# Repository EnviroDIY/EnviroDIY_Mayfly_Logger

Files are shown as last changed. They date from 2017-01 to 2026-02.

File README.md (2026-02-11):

EnviroDIY Mayfly Data Logger
==============
The [EnviroDIY™ Mayfly Data Logger](http://envirodiy.org/mayfly/) is an Arduino-framework microcontroller board designed specifically for environmental Internet of Things (IoT) applications with the goal to facilitate professional-quality, do-it-yourself (DIY) environmental science and monitoring.

This [EnviroDIY_Mayfly_Logger Github repository](https://github.com/EnviroDIY/EnviroDIY_Mayfly_Logger) provides hardware design files and example code sketches, the [EnviroDIY community](https://www.envirodiy.org) provides support via project posts and forums, and the [Mayfly Logger board is available for purchase on the [EnviroDIY Shop](https://www.envirodiy.org/shop/) for user convenience.

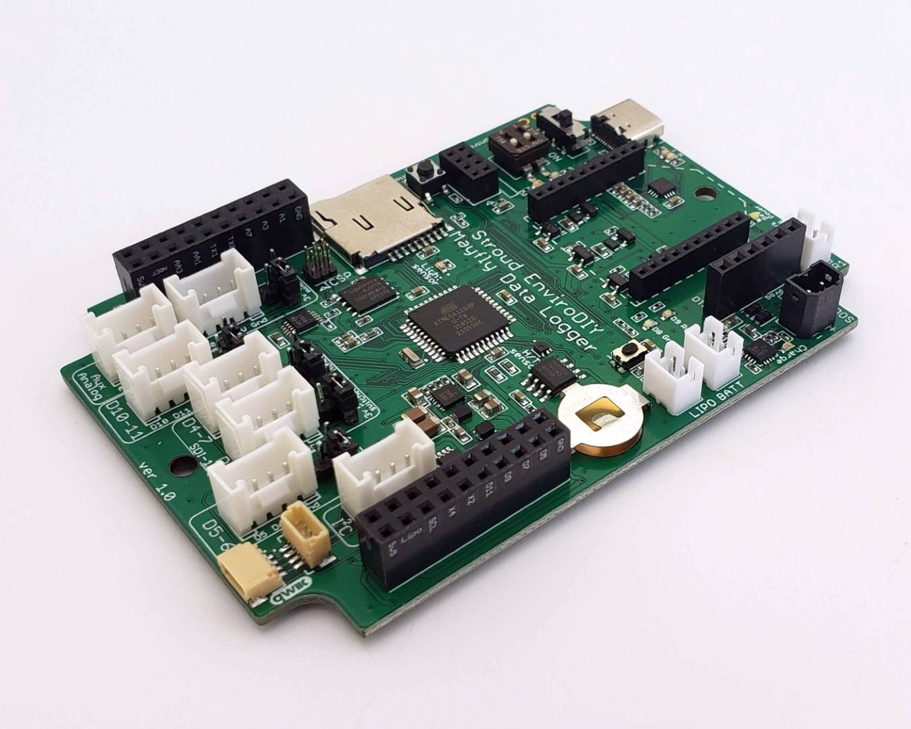
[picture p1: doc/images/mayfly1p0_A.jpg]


## Features:

- ATmega1284p processor
    - 128kB program (flash) memory, 16kB RAM
    - 2 UART, 1 I2C, 1 SPI connection
    - 32 total I/O pins
    - 3.3V, 8MHz operating frequency
- Integrated 6V solar lipo battery charger
- Precise real time clock (RTC, [DS3231](https://datasheets.maximintegrated.com/en/ds/DS3231.pdf)) with separate power supply
- Auxillary 16 bit ADC ([TI ADS1115](http://www.ti.com/lit/ds/symlink/ads1114.pdf))
- FTDI chip for USB communication via USB-C port
- microSD memory card socket
- XBee radio/wifi/cellular module socket
- 7 [Grove](http://wiki.seeedstudio.com/Grove_System/) connectors with access to I2C, auxillary ADC, and digital pins
- 0.5A switchable power supply for sensors at 3.3V and 5V, and 0.15A at 12V
- On-board power switch
- Two controllable LED's (red and green)
- One programmable push-button
- Onboard humidity/temperature sensor and analog light sensor
- Onboard auxiliary 8MB flash memory chip

## Pin-out for v1.x

| Pin Number[s] | Function             | Access                                 | Notes |
|---------------|----------------------|----------------------------------------|-------|
| D0/D1         | Serial Rx/Tx (UART)  | Connected to FTDI for USB programming  | Also accessible via programming port, 20 pin header, and XBee socket via SJ8/9 |
| D2/D3         | Serial1 Rx/Tx (UART) | XBee socket Din/Dout (pins 2/3)        | Also accessible via 20 pin header, can be disconnected from XBee socket via SJ8/9 |
| D19           | XBee CTS             | XBee socket CTS (pin 12)               | Also accessible via 20 pin header |
| D20           | XBee RTS             | XBee socket RTS (pin 16)               | Also accessible via 20 pin header |
| D23           | XBee DTR             | XBee socket DTR (pin 9)                | Also accessible via 20 pin header |
| A5=D29*       | XBee Assoc or RI     | XBee socket Assoc or RI (pin 15 or 20) | Not connected to XBee socket by default, use SJ7 to connect; Also accessible via 20 pin header |
| D16/D17       | I2C SCL/SDA ("Wire") | Grove connector                        | Also accessible via 20 pin header |
| D13/D14/D15   | SPI MOSI/MISO/SCK    | microSD card slot & SPI header         |  |
| D12           | microSD chip select  | microSD card slot & SPI header         |  |
| D18           | SD card detect OR RTC 32KHz | 20 pin header                   | Not connected to either SD or RTC by default, use SJ6 for RTC or SJ10 for SD, _do not use both_ |
| A7=D31 _or_ D10 | RTC Interrupt      | 20 pin header                          | A7 is connected to RTC interrupt by default; Use SJ1 to disconnect A7 and/or to connect D10 |
| D22           | Switched power/LED4  | Switched power on all Grove ports      | Pin is not directly accessible, only switched power; Cut SJ3 to disconnect LED4 (red) |
| D21           | user push button     | 20 pin header                          | Cut SJ to disconnect button |
| D8            | LED1 (green)         | 20 pin header                          |  |
| D9            | LED2 (red)           | 20 pin header                          |  |
| A6=D30        | Battery measurement  | None                                   | Connected via voltage divider |
| D4-7, D10-11  | General Purpose I/O  | Grove connector; 20 pin header         |  |
| AA0-AA3       | Auxilliary ADC       | Grove connector; 20 pin header         | Connected to _Auxillary_ adc (TI ADS1115), not to Mayfly analog pins |

## Solder Jumper Connections for v1.x

| Number | Function                        | Default Connection                |
|--------|---------------------------------|-----------------------------------|
| SJ1    | Connect to interrupt from RTC   | Pin A7 connected to RTC interrupt       |
| SJ2    | Disconnect D21 from user button | Pin D21 is connected to button (closed) |
| SJ3    | Disconnect D22 from LED3        | Pin D22 is connected to LED3 (closed)   |
| SJ4    | Disconnect LED4 from solar      | LED4 indicates solar charging status (closed) |
| SJ7    | Pin A5 to XBee ASSOC _or_ RI    | Not connected (all pads open)                 |
| SJ8    | XBee Din to TX0/TX1             | XBee Din connected to TX1                     |
| SJ9    | XBee Dout to RX0/RX1            | XBee Dout connected to RX1                    |
| SJ12   | D10 external pull-up            | D10 (INT2) is not pulled up externally (open) |

## Programming

Mayfly Data Logger can be programmed using standard Aruduino code and community libraries via the [Arduino Integrated Development Environment (IDE) software](https://www.arduino.cc/en/Main/Software) or the more powerful [PlatformIO](https://platformio.org) extensions for [Visual Studio Code](https://code.visualstudio.com/) or [Atom](https://atom.io/).

To use the Mayfly with the Arduino IDE you must add "EnviroDIY ATmega Boards" using the Tools > Board > Boards Manager as described in the [Mayfly Data Logger Software](http://envirodiy.org/mayfly/software/) post

No addition set-up is required to use the PlatformIO.
The proper enviroment settings for the Mayfly in a platformio.ini file are:

```ini
[env:mayfly]
platform = atmelavr
board = mayfly
framework = arduino
```

## Additional Resources and Links

- Read the [Getting Started With the Mayfly Data Logger](http://envirodiy.org/mayfly/) page on the EnviroDIY community website for guidance for beginners with the Mayfly, sensor station maintence, and data management.
- Make use of the [The EnviroDIY Mayfly Data l=Logger Forum](https://www.envirodiy.org/forum/mayfly-data-logger/) to ask and answer questions about the Mayfly
- Learn Mayfly basics following our [Mayfly Data Logger Software](http://envirodiy.org/mayfly/software/) post and running the example and workshop code sketches, using the Arduino IDE (from File > Sketchbook), from our [EnviroDIY_Mayfly_Logger > examples](https://github.com/EnviroDIY/EnviroDIY_Mayfly_Logger/tree/master/examples) or [EnviroDIY_Mayfly_Logger > workshop](https://github.com/EnviroDIY/EnviroDIY_Mayfly_Logger/tree/master/workshop) folders.
- Advance your capabilities to deploy solar-powered environmental monitoring stations with our [LearnEnviroDIY tutorial](https://envirodiy.github.io/LearnEnviroDIY/)
- Utilize the [ModularSensors](https://github.com/EnviroDIY/ModularSensors) code library and other [EnviroDIY libraries on GitHub](https://github.com/EnviroDIY) for datalogging built around the Mayfly
- Find and attend a training workshop for do-it-yourself environmental monitoring built around the Mayfly by contacting the Stroud Water Research Center's [citizen science outreach](https://stroudcenter.org/people/bressler/) or [education](https://stroudcenter.org/education/contact/) departments.

## Design Files & Further Documentation

We share our EnviroDIY Mayfly logger hardware design files and documentation in this repository's [Hardware Design Files](hardware) pages and [Documentation](doc) pages.

## License
Software sketches and code are released under the BSD 3-Clause License -- See [LICENSE.md](https://github.com/EnviroDIY/EnviroDIY_Mayfly_Logger/blob/master/LICENSE.md) file for details.

Documentation is licensed as [Creative Commons Attribution-ShareAlike 4.0](https://creativecommons.org/licenses/by-sa/4.0/) (CC-BY-SA) copyright.

Hardware designs shared are released, unless otherwise indicated, under the [CERN Open Hardware License 1.2](https://www.ohwr.org/projects/cernohl/wiki) (CERN_OHL).

## Credits
[EnviroDIY](http://envirodiy.org/)™ is presented by the Stroud Water Research Center, with contributions from a community of enthusiasts sharing do-it-yourself ideas for environmental science and monitoring.

[Shannon Hicks](https://github.com/s-hicks2) is the primary developer of the EnviroDIY Mayfly Data Logger hardware, with input from many [other contributors](https://github.com/EnviroDIY/EnviroDIY_Mayfly_Logger/graphs/contributors).

The Mayfly was developed based on the [SODAQ Mbili board](https://support.sodaq.com/sodaq-one/sodaq-mbili-1284p/) hardware and the [SODAQ Mbili bootloader](https://github.com/SodaqMoja/HardwareMbili) software, designed by Gregory Knauff (GKNFF).

This project has benefited from the support from the following funders:

* William Penn Foundation
* US Environmental Protection Agency (EPA)
* National Science Foundation, awards [EAR-0724971](http://www.nsf.gov/awardsearch/showAward?AWD_ID=0724971), [EAR-1331856](http://www.nsf.gov/awardsearch/showAward?AWD_ID=1331856), [ACI-1339834](http://www.nsf.gov/awardsearch/showAward?AWD_ID=1339834)
* Stroud Water Research Center endowment

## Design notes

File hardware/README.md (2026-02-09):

Hardware Design Files
==============

Here we provide EnviroDIY Mayfly design files including:
- EAGLE PCB electronic design files for use with the EAGLE electronic design automation (EDA) software (a [free maker edition](https://www.autodesk.com/products/eagle/compare) is available).
- Board schematic images, for versions 0.3, 0.4, 0.5, 0.5b, 1.0, 1.1revA, and 1.1revB.

See our [Documentation](https://github.com/EnviroDIY/EnviroDIY_Mayfly_Logger/tree/master/doc) pages for a [Feature List](https://github.com/EnviroDIY/EnviroDIY_Mayfly_Logger/blob/master/doc/Intro_GettingStarted.md), for details on [Board Features](https://github.com/EnviroDIY/EnviroDIY_Mayfly_Logger/blob/master/doc/Hardware_BoardFeatures.md), and for [Jumper Settings](https://github.com/EnviroDIY/EnviroDIY_Mayfly_Logger/blob/master/doc/Hardware_JumperSettings.md).

For questions, use our Q&A forum at https://envirodiy.org/forum/mayfly/.

## Hardware Design Credits

The Mayfly Logger was developed by [Shannon Hicks](https://github.com/s-hicks2) and based on the [SODAQ Mbili board](https://support.sodaq.com/sodaq-one/sodaq-mbili-1284p/) hardware and the [SODAQ Mbili bootloader](https://github.com/SodaqMoja/HardwareMbili) software designed by Gregory Knauff (GKNFF).

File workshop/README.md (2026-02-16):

Example sketches used in workshops with the EnviroDIY Mayfy Data Logger v1.x boards.

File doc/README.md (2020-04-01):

Documentation
==============
The documentation contained in this folder are based on documentation provided by the EnviroDIY community website at https://www.envirodiy.org/mayfly/. These are:

- #### [Hardware: Feature List](https://github.com/EnviroDIY/EnviroDIY_Mayfly_Logger/blob/master/doc/Intro_GettingStarted.md)
  - #### [Board Features](https://github.com/EnviroDIY/EnviroDIY_Mayfly_Logger/blob/master/doc/Hardware_BoardFeatures.md)
  - #### [Jumper Settings](https://github.com/EnviroDIY/EnviroDIY_Mayfly_Logger/blob/master/doc/Hardware_JumperSettings.md)

- #### [Software](https://github.com/EnviroDIY/EnviroDIY_Mayfly_Logger/blob/master/doc/Software_Intro.md)

See this repository's [Hardware Design Files](hardware) pages for [Board schematics](https://github.com/EnviroDIY/EnviroDIY_Mayfly_Logger/blob/master/hardware) and [EAGLE PCB electronic design files](https://github.com/EnviroDIY/EnviroDIY_Mayfly_Logger/blob/master/hardware/Mayfly_v0p5b).

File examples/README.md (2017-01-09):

Example Arduino Sketches for the Mayfly Board
==============

All of the Mayfly boards have been pre-programmed with an initial demonstration sketch, named "initial\_demo\_blink_temperature".  When you first connect power to the board, and turn the board on (switch on upper left) you will see the red and green LEDs blinking.

You can also see the real-time temperature of your Mayfly board if you [connect the Mayfly to your computer and configure the Arduino IDE to communicate with it](https://github.com/EnviroDIY/Arduino_boards). Once the Arduino IDE is configured to communicate with your Mayflay board, open the [Serial Monitor button (button on upper right of any sketch)](https://lh6.googleusercontent.com/GO9HQ1q3v4ho-H7ZqP55cQ4o_nLdyYpkCauIWOvN5xrQAMNIfgeiu_LiRTfAN2yruvjBLGMNrACzWffwhlM5ADSem35dDPpI9Mj5WWN-l8YSizSh-3HwvPEwtzAo3o0ZZjJgAyw), and change the serial communication rate at 57600 baud. You will see the current board temperature as measured by the DS3231 Real Time Clock chip's internal temperature sensor, updated every second.

Try out some of the other examples sketches shared here!

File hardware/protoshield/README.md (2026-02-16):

EagleCAD files for the Mayfly Protoshield v1 (discontinued in 2020)

NOTE:  This ProtoShield is only compatible with the older Mayfly v0.5b boards.  It is not compatible with the newer Mayfly v1.0 or v1.1 board due to changes in the pinouts of the headers.  Do not attempt to use this ProtoShield with a Mayfly v1.0 or v1.1 board or damage to the Mayfly and/or ProtoShield will occur.

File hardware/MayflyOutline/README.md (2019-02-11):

EagleCAD file for basic ouline of the Mayfly board with headers (v0.3, v0.4, v0.5, v0.5b)

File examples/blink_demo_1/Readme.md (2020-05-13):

# Blinking LED's: Version 1

This example program:
- Turns on an LED on for one second, then off for one second, repeatedly.
- Introduces use of variables.
- Includes Serial Monitor readout in setup function.

This is blink demo is designed for first-time users of Arduino and the EnviroDIY Mayfly logger.

The Mayfly has two LED lights attached to digital pins 8 and 9.
Both lights can be controlled using code with the ```pinMode``` and ```digitalWrite``` functions.

## Stepping through the code

Arduino sketches (really c++ programs) begin with a list of the outside libraries needed to run the sketch.
These libraries must be installed on your .../Arduino/libraries directory for the sketch to run.
This example only uses one library, the Arudino framework library (```Arduino.h```).
We include that library with the following code:
```cpp
#include <Arduino.h>
```

After including the Arduino framework, we name some "global variables" for the sketch.
This variables list is located before the functions and defines the variables for the sketch.
Variables are useful for assigning information once at the beginning of a sketch, because most sketches will need to repeat information like pin locations.
Notice that the sketch re-uses the value ```delayTime``` four times.
The text ```int``` before the name of the variable specifies integer data type.

Try modifying the delay time and LED pin and re-running the sketch.
```cpp
int delayTime = 1000;   // milliseconds, so 1000 = one second
```

Assign pin numbers for built-in LEDs.
```cpp
int LED_BUILTIN_green = 8;  // Mayfly has a green LED connected to digital pin 8
int LED_BUILTIN_red = 9;    // Mayfly has a red LED connected to digital pin 9
```

The "setup" function runs once when you press reset or power the board.
The "returned value" for this function is "void", which means it doesn't return a value, the function simply performs an action.
```cpp
void setup ()
{
    pinMode(LED_BUILTIN_green, OUTPUT);  // set the pin as output to turn on the LED
    pinMode(LED_BUILTIN_red, OUTPUT);    // all you need to set up the LED blink
    delay(delayTime);
    Serial.println("Mayfly: Blink demo 1");  // sends a message to the Serial Monitor
    delay(delayTime);
}
```

The "loop" function runs over and over again.
It performs an action wouthout returning a value, so "void" is once again used in the function declaration.
```cpp
void loop ()
{
    digitalWrite(LED_BUILTIN_green, HIGH); // turn the green LED on (HIGH is the voltage level)
    digitalWrite(LED_BUILTIN_red, LOW);    // and turn the red LED off (LOW is the voltage level)
    delay(delayTime);                      // wait for the time specified in delayTime variable
    digitalWrite(LED_BUILTIN_green, LOW);  // now turn the green LED off by making the voltage LOW
    digitalWrite(LED_BUILTIN_red, HIGH);   // and turn the red LED on
    delay(delayTime);                      // wait for the time specified in delayTime variable
}
```

## Notes

This demo assumes you have installed the proper drivers to connect to the Mayfly.
If you need a resource for getting started with Arduino, the tutorial by Adafruit at https://learn.adafruit.com/series/ladyadas-learn-arduino will get you connected and running a blink demo in about an hour.

To run this demo you will need to first connect to the Mayfly by specifying your board under
Tools>Board (select appropriate Mayfly board) and specifying which communication port to use
under Tools>Port.

Once connected to the Mayfly, you need to Verify/Compile the sketch by clicking the checkmark at the top, left corner of the Arudino app window. If there is an error, it will appear (in orange) below.
If there are no errors, the window color will not change and it will read "Done compiling."
Always compile before uploading a sketch to your Arduino.
Once compiled, click on the right arrow button to upload the sketch to the Mayfly.
If it worked, the LED lights on the board will begin to blink.

## Credits

Original sketch:
- modified 8 May 2014 by Scott Fitzgerald
- modified 2 Sep 2016 by Arturo Guadalupi
- modified 8 Sep 2016 by Colby Newman for Mayfly:
- modified 7 Jun 2017 by Beth Fisher github.com/fisherba

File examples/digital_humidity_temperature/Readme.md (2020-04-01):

# Reading digital temperature and humidity

This example program:
- Communicates with a digital temperature/humidity board (DHT11)
- Writes the output to the serial port at one second intervals

Written for Mayfly logger and Grove digital temperature/humidity board based on the AOSong DHT (DHT11), with options for DHT 21 and 22.

## Physical connections

- Connect pin 1 (on the left) of the sensor to +5V
- Connect pin 2 of the sensor to whatever your DHTPIN is
- Connect pin 4 (on the right) of the sensor to GROUND
- Connect a 10K resistor from pin 2 (data) to pin 1 (power) of the sensor

## Stepping through the code

Arduino sketches (really c++ programs) begin with a list of the outside libraries needed to run the sketch.
These libraries must be installed on your .../Arduino/libraries directory for the sketch to run.
This example only uses two libraries, the Arudino framework library (```Arduino.h```) and the Adafruit library for the AOSong DHT (```DHT.h```).
We use the include that library with the following code:
```cpp
#include <Arduino.h>
#include <DHT.h>
```

After including the libraries, we define exactly which type of sensor we're using and the pin it is connected to.
We then create an "object" in the processor's memory representing the functionality of the DHT sensor.
```cpp
#define DHTPIN 10       // Specifies the pin connected to the DHT signal.
#define DHTTYPE DHT11   // DHT 11

DHT dht(DHTPIN, DHTTYPE);
```

The "setup" function runs once when you press reset or power the board.
The "returned value" for this function is "void", which means it doesn't return a value, the function simply performs an action.
In this setup function, we are providing power to the DHT sensor by turning on pin 22.
We are also writing a note to the serial port to appear on the serial monitor.
The last function performs necessary setup for the DHT.
Because we are using a library of functions to communicate with the DHT, we do not need to specify exactly what commands are needed to prepare the DHT.
We call the begin function for the dht object in memory and take advantage of the set-up code provided by that library.
```cpp
void setup()
{
    pinMode(22, OUTPUT);      // pin D22 is the enable line for the Mayfly's switched 3.3/5v power lines
    digitalWrite(22, HIGH);   // set this pin high and leave it on for the rest of the sketch
    delay(200);
    Serial.begin(57600);
    Serial.println("Digital Humidity/Temperature");

    dht.begin();
}
```

The "loop" function runs over and over again.
It performs an action wouthout returning a value, so "void" is once again used in the function declaration.
As in the set-up, we rely on the DHT library to figure out the details of talking to the DHT and call that libraries functions to get the results of the reading.
We print the readings to the serial monitor.
```cpp
void loop()
{
    // Reading temperature or humidity takes about 250 milliseconds
    // Sensor readings may also be up to 2 seconds old
    float h = dht.readHumidity();
    float t = dht.readTemperature();

    // check if returns are valid, if they are NaN (not a number) then something went wrong
    if (isnan(t) || isnan(h))
    {
        Serial.println("Failed to read from DHT");
    }
    else
    {
        Serial.print("Humidity: ");
        Serial.print(h);
        Serial.print(" %\t");
        Serial.print("Temperature: ");
        Serial.print(t);
        Serial.println(" *C");
    }
}
```

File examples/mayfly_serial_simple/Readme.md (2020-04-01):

# A simple serial example

This example program:
- Sends data to the computer via the FTDI chip on Serial
- Sends data to an XBee via Serial 1

## Stepping through the code

Arduino sketches (really c++ programs) begin with a list of the outside libraries needed to run the sketch.
These libraries must be installed on your .../Arduino/libraries directory for the sketch to run.
This example only uses one library, the Arudino framework library (```Arduino.h```).
We use the include that library with the following code:
```cpp
#include <Arduino.h>
```

The "setup" function runs once when you press reset or power the board.
The "returned value" for this function is "void", which means it doesn't return a value, the function simply performs an action.
In this setup function, we are deciding at what speed the board will communicate and printing out text.
```cpp

void setup()
{
  Serial.begin(57600);  // Start the serial connection with the computer (UART-0)

  Serial1.begin(9600);  // Start the connection on the Mayfly's Xbee port (UART-1)
}

```

The "loop" function runs over and over again.
It performs an action wouthout returning a value, so "void" is once again used in the function declaration.
This functio merely prints some text to the serial monitor and to the XBee socket with a short delay in between.
```cpp
void loop()
{

 Serial.println("This is Serial Data printed to the computer");

 delay(500);

 Serial1.print("This is Serial Data sent to the Xbee port");

 delay(5000);
}
```

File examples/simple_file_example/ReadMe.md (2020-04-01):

# Simple File Example

This example program demonstrates reading the battery voltage on the LiPo attached to the Mayfly and writing that value to a file on a SD card.

NOTE:  This program is for demonstration only.  It is NOT intended to be used for environmental monitoring.  It does not contain any of the necessary code to allow the Mayfly to sleep and reduce power between readings.

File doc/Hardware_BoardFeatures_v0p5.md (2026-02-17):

Board Features for v0.5b
==============
The Mayfly Data Logger board has many unique features and hardware options. Learn more below!

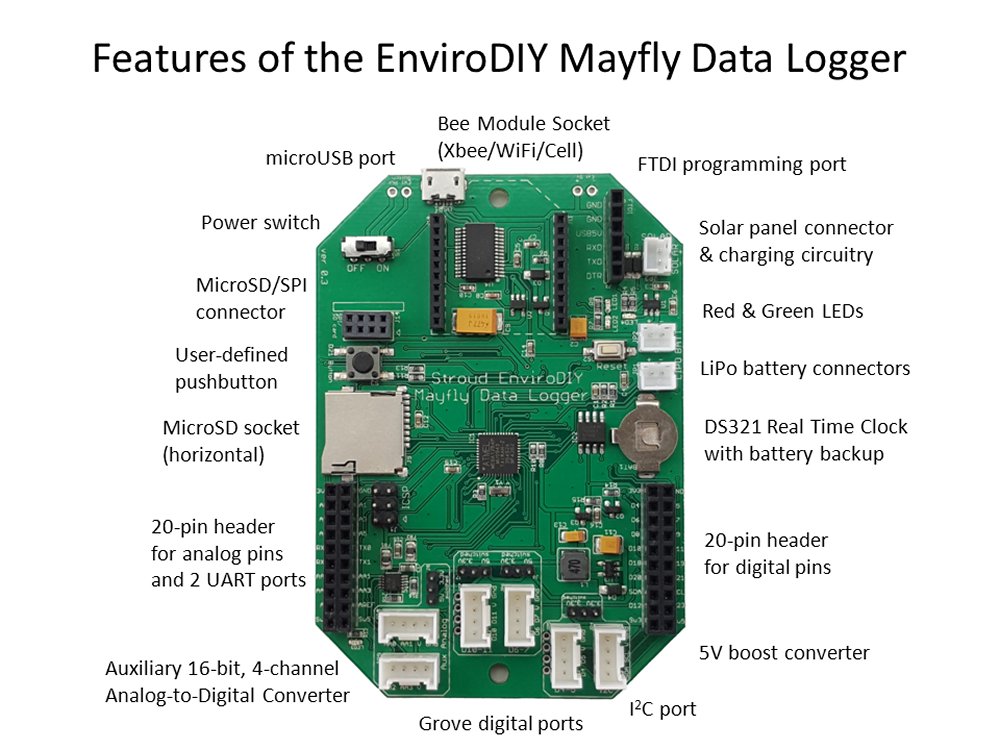
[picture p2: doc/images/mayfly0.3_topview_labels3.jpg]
Mayfly v0.3 Top View with Labels


## Features of the EnviroDIY Mayfly Data Logger version 0.5b

The microUSB port is used to program the Mayfly via your computer.
Once the board has been programmed, you can also supply power to the Mayfly with any microUSB cable or mobile phone charger that provides 5vDC.

The Bee socket is compatible with any module that use the standard Bee connection footprint.
Modules include Xbee radio modules, GPRSBee cell phone board, and other modules for WiFi or Bluetooth communication.

A 6-pin header is available for programming the board via a standard FTDI interface board or programming cable.
Be sure to observe the polarity and connect the FTDI adapter in the right orientation.

Any 6-volt solar panel can be connected to the JST socket for charging a standard 3.7v LiPo battery.
A yellow LED will light up whenever there is sufficient sunlight to charge the battery.

Two LEDS (one green, one red) are connected to pins D8 (green) and D9 (red) for full user control.

Two JST connectors are labeled LiPo (lithium polymer) battery power connections.
Connect a standard 3.7v LiPo battery to either port.
You should only connect one battery to the Mayfly.
The second port is for devices like the GPRSbee that need a direct connection to the battery.
More information about using the GPRSbee will be provided soon.

The DS3231 Real Time Clock chip needs a small battery to keep it’s clock running when the Mayfly isn’t powered by a main battery.
Insert a CR1220 3v lithium battery (with the + side facing up).
Users who don’t want to keep the RTC backed up can omit the battery.

Two 20-pin headers with standard 0.1″ pin spacing provide access to all of the available pins.

A voltage boost circuit provides a 5 volt supply that can be switched on or off by using pin D22.
This pin is also used to turn the “3.3v_Switched” output on or off.

Grove connectors provide easy interface to 4 groups of digital pins. Three of the connectors contain digital pins (4, 5, 6, 7, 10, and 11) and the forth connector is for I2C protocol.
Note:  on board versions 0.3 and 0.4, the I2C connector has the proper pin order found on all Grove I2C ports, but the white silkscreen printing on the board has the SDA and SCL pins reversed.
The pins are correct, only the printing is swapped.
The printing is correct on version 0.5.

Two more Grove connectors interface with the ADS1115 auxiliary 16-bit A/D converter.

The data card socket on the Mayfly accepts standard microSD memory cards.

The pushbutton is connected to digital pin D21.
Users can have their sketch look for a state change on that pin to provide input to the system.

A small 2×4 header allows users to connect the custom Mayfly microSD right-angle adapter board.
This handy accessory allows you to easily access the memory card when the Mayfly is mounted in an enclosure where the usual horizontal slot is inaccessible.
Do not use a memory card in both sockets at the same time.
Users could also build their own custom adapter boards for this header since it breaks out all of the necessary SPI pins.

## New features on version 0.5:
In March 2017, we released version 0.5.
Here are the main difference between 0.5 and the earlier versions:

- Separate 3.3v regulator on the Switched3.3v bus (makes the board more stable when switching loads on and off, and increase current output available to the load with a max output of 500ma)
- New 5v-boost regulator (SC4503 replaces the obsolete NCP1402)
- Onboard pullup resistor (1M ohm) available via jumper SJ12 for connecting D10 to the pullup (useful for using D10 as a hardware interrupt)
- External voltage input range improved – now accepts 4 to 12v.
A small slide switch on the top of the board allows you to select the usual USB/Lipo power option, or you can select an external voltage source to power the board.
To prevent over-voltage damage, the USB port is disconnected from the Mayfly when the switch is set to “Ext”.
If you are using the Mayfly with an external battery and then want to reprogram the Mayfly, you’ll need to slide the switch to “USB/Lipo” in order to program the board.
Then slide it back to “Ext” to power the board via your external source.
If you have a Lipo battery connected to the “Lipo Batt” JST headers, be sure to keep the slide switch in the “USB/Lipo” position or the board will not be powered.

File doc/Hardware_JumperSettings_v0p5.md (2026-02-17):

Jumper settings for v0.5b
==============
On the back of the Mayfly v0.5b board, there are 12 user-configurable solder jumpers to allow the user to configure the board with different options.

## Jumpers on back of Mayfly board

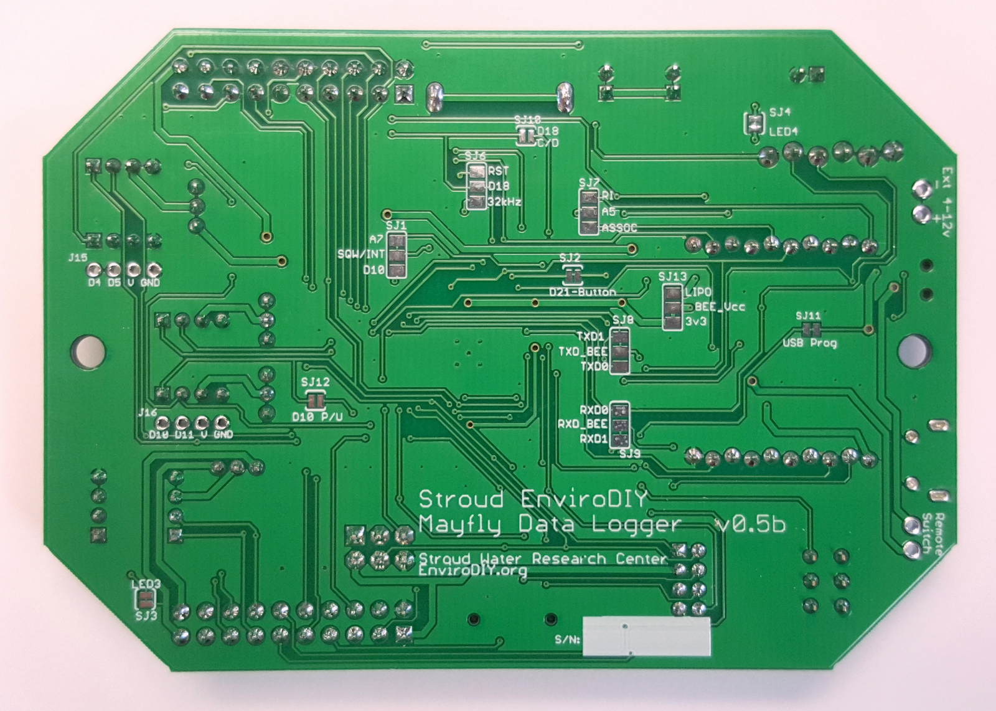
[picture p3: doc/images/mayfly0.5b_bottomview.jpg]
Mayfly v0.5b Bottom View


On the back of the Mayfly v0.5b board, there are 12 user-configurable solder jumpers.

SJ1:  Connects the RTC Square-Wave Interrupt line to pin A7 (or D10 on board v0.4). This allows the RTC to wake up the Mayfly from sleep mode. Default position is connected to A7.
Cut the trace to free up pin A7 for something else. Add solder bridge to connect center pad to D10 if you’d like to use the D10 hardware interrupt.

SJ2:  Connects the pushbutton to pin D21.
Default position is ON.
Cut the trace to free up D21.

SJ3:  Enables the red LED to be lit when the switched 3.3v line is turned on.
Default position is ON.
Cut the trace to disable the LED.

SJ4:  Enables the yellow LED that is lit whenever the lipo battery is being charged.
Default position is ON.
Cut the trace to disable the LED.

SJ5:  Enables the 5v boost circuitry.
Default position is ENABLED.
Cut the trace and solder the middle pad to the DISABLE pad to deactivate the 5v boost circuit.
Note:  This jumper has been removed on board version 0.5 and later

SJ6:  Connects the RTC Reset or 32khz signal to pin D18.
Default position is NONE.
Solder the middle pad to only one other pad if needed.
Note:  SJ6 and SJ10 are both used for configuring inputs to D18.
Do not use SJ10 if you select a setting for SJ6.

SJ7:  Connects the Bee socket Ring Indicator or Associate lines to A5.
Default position is NONE.

SJ8:  Connects the Bee socket TX signal to Mayfly TXD0 (UART 0) or TXD1 (UART 1).
Default position is TXD1

SJ9:  Connects the Bee socket RX signal to Mayfly RXD0 (UART 0) or RXD1 (UART 1).
Default position is RXD1

SJ10:  Connects the microSD socket’s Card Detect line to D18.
Default position is OFF.
Solder this jumper together if you want to be able to sense a memory card in either the horizontal socket or the vertical adapter board.
Note:  SJ6 and SJ10 are both used for configuring inputs to D18.
Do not use SJ6 if you select a setting for SJ10.

SJ11:  Controls power to the FT232RL USB chip.
Default position is ON.
Cut this trace if you do not want to use the USB port for programming.

SJ12:  *Only on board v0.5 and later*, this jumper allows you to easily connect the onboard 1M-ohm pullup resistor to D10.
Default position is OFF. Add a solder bridge if you want to connect D10 to the onboard pullup resistor.
This is handy for using D10 as a hardware interrupt.
DO NOT use this jumper if you have modified SJ1 to use D10 as the RTC interrupt.
Also, DO NOT use this jumper if you are using D10 for any other type of input besides something that needs the pullup.

SJ13:  *Only on board v0.5b and later*, this jumper allows you to select the power source for the Bee socket’s Vcc pin (Bee pin 1). The default setting is that Bee is powered by the Mayfly’s main 3.3v Vcc supply.
By cutting the SJ13 trace and soldering the middle pad to the LiPo setting, you can connect the Bee Vcc pin directly to the Mayfly’s LiPo battery input.

## Jumpers on Grove Ports

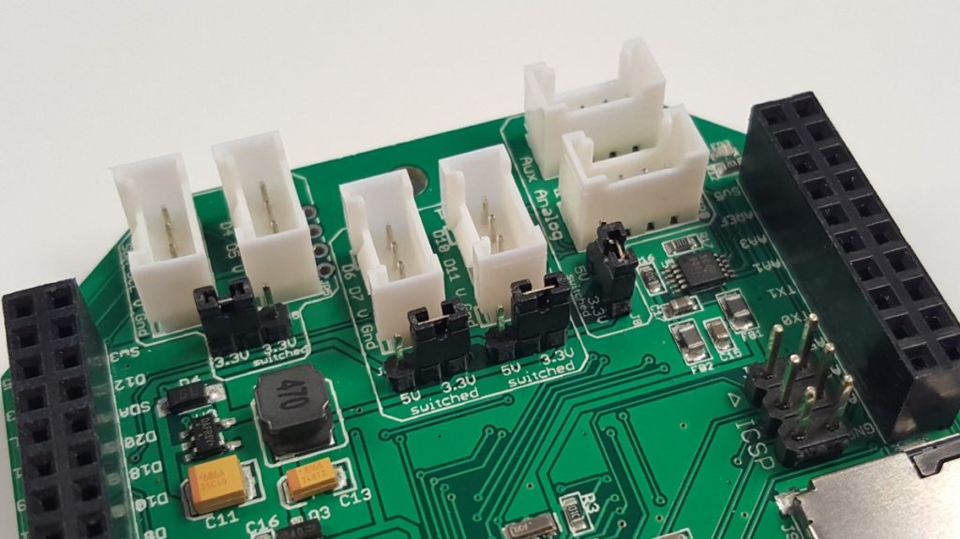
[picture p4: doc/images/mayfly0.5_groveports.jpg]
Mayfly v0.5b Grove Ports


On the front of the board, there are 4 small 3-pin headers next to the Grove connectors.
These headers allow you to select what voltage signal goes on the V line of the Grove connector.

The 2 Grove connectors labeled “I2C” and “D4-5” can be powered by either 3.3v constantly or the switchable 3.3v signal (controlled by D22).

The 2 Grove connectors labeled “D6-7” and “D10-11”  can be powered by either the switchable 3.3v line or the switchable 5v line (both controlled by D22)

The 2 Grove connectors for the Auxiliary Analog converter can be powered by either the switchable 3.3v line or the switchable 5v line (both controlled by D22)

These are 2.0mm pitch jumpers, so a standard 0.1-inch jumper will not fit securely.

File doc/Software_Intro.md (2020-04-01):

Mayfly Data Logger Software
==============
To program the EnviroDIY Mayfly, you can use the free Arduino IDE programming software.  Download the latest version from Arduino.cc.  If you already have the IDE installed on your computer, ensure that you are using version 1.6.5 or newer.

Once the Arduino IDE is installed, you will need to add the Mayfly board to the list of available boards.  To do this, start the Arduino software, then click on the “File” menu, then “Preferences” and paste the following URL into the box labeled “Additional Boards Manager URLs”:

```
https://raw.githubusercontent.com/EnviroDIY/Arduino_boards/master/package_EnviroDIY_index.json
```

Then back in the IDE, click on Tools > Board > Boards Manager. Use the dropdown box to select “Contributed”. You should then see an option for “EnviroDIY ATmega Boards”. Click the Install button to add the EnviroDIY boards to your IDE.

Now when you click Tools > Board you will see the EnviroDIY Mayfly 1284P listed either at the top or bottom of your list of available boards.

## Sample Sketch

All of the Mayfly boards have been pre-programmed with a sample sketch.  When you first connect power to the board, you will see the red and green LEDs blinking.  If you connect the Mayfly to your computer and open a serial terminal window at 57600 baud, you will see the current temperature as measured by the DS3231’s internal temperature sensor, updated every second.

This sketch uses a library called Sodaq_DS3231.h which is necessary to interact with the DS3231 RTC chip.  The Mayfly is based on the SODAQ Mbili, so the SODAQ DS3231 library is recommended.

```cpp
#include <Wire.h>
#include "Sodaq_DS3231.h"

int State8 = LOW;
int State9 = LOW;

int LEDtime = 1000;   //milliseconds

void setup ()
{
    pinMode(8, OUTPUT);
    pinMode(9, OUTPUT);
    Serial.begin(57600);
    Wire.begin();
    rtc.begin();

    Serial.println("EnviroDIY Mayfly: Blink demo with serial temperature");     
}

void loop ()
{
    if (State8 == LOW) {
      State8 = HIGH;
    } else {
      State8 = LOW;
    }
    digitalWrite(8, State8);
    State9 = !State8;
    digitalWrite(9, State9);

    rtc.convertTemperature();             //convert current temperature into registers
    Serial.print(rtc.getTemperature(),2); //read registers and display the temperature
    Serial.println("deg C");

    delay(LEDtime);
}
```

## Other sketches

- Blinking LEDs
- [Battery measurement](https://github.com/EnviroDIY/EnviroDIY_Mayfly_Logger/tree/master/examples/battery_measurement)
- Simple file example
- Digital humidity/temperature sensor (with switched 3.3v power)
- Serial communication
- Ultrasonic sensor
- Sleeping Mayfly logger

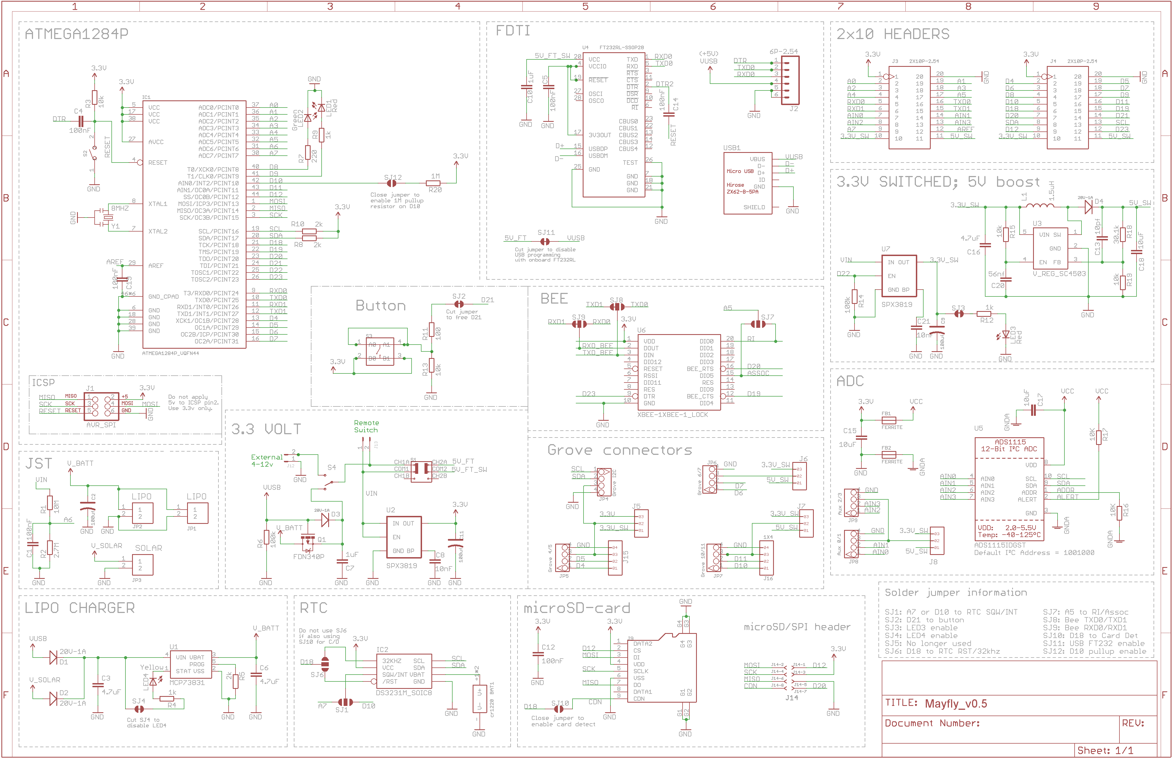
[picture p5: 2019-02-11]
hardware/Mayfly_0p5/mayfly_v0p5_schematic.png

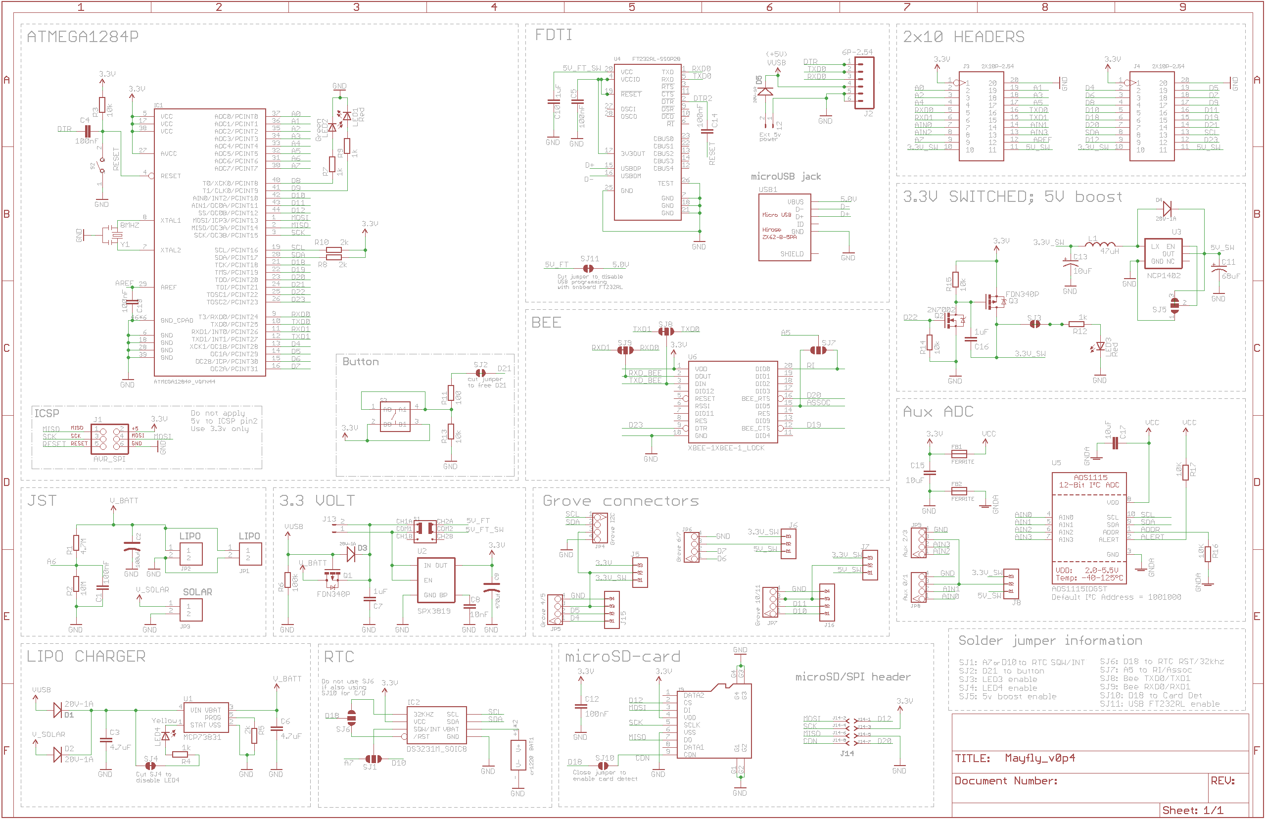
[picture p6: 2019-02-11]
hardware/Mayfly_0p4/mayfly_v0p4_schematic.png

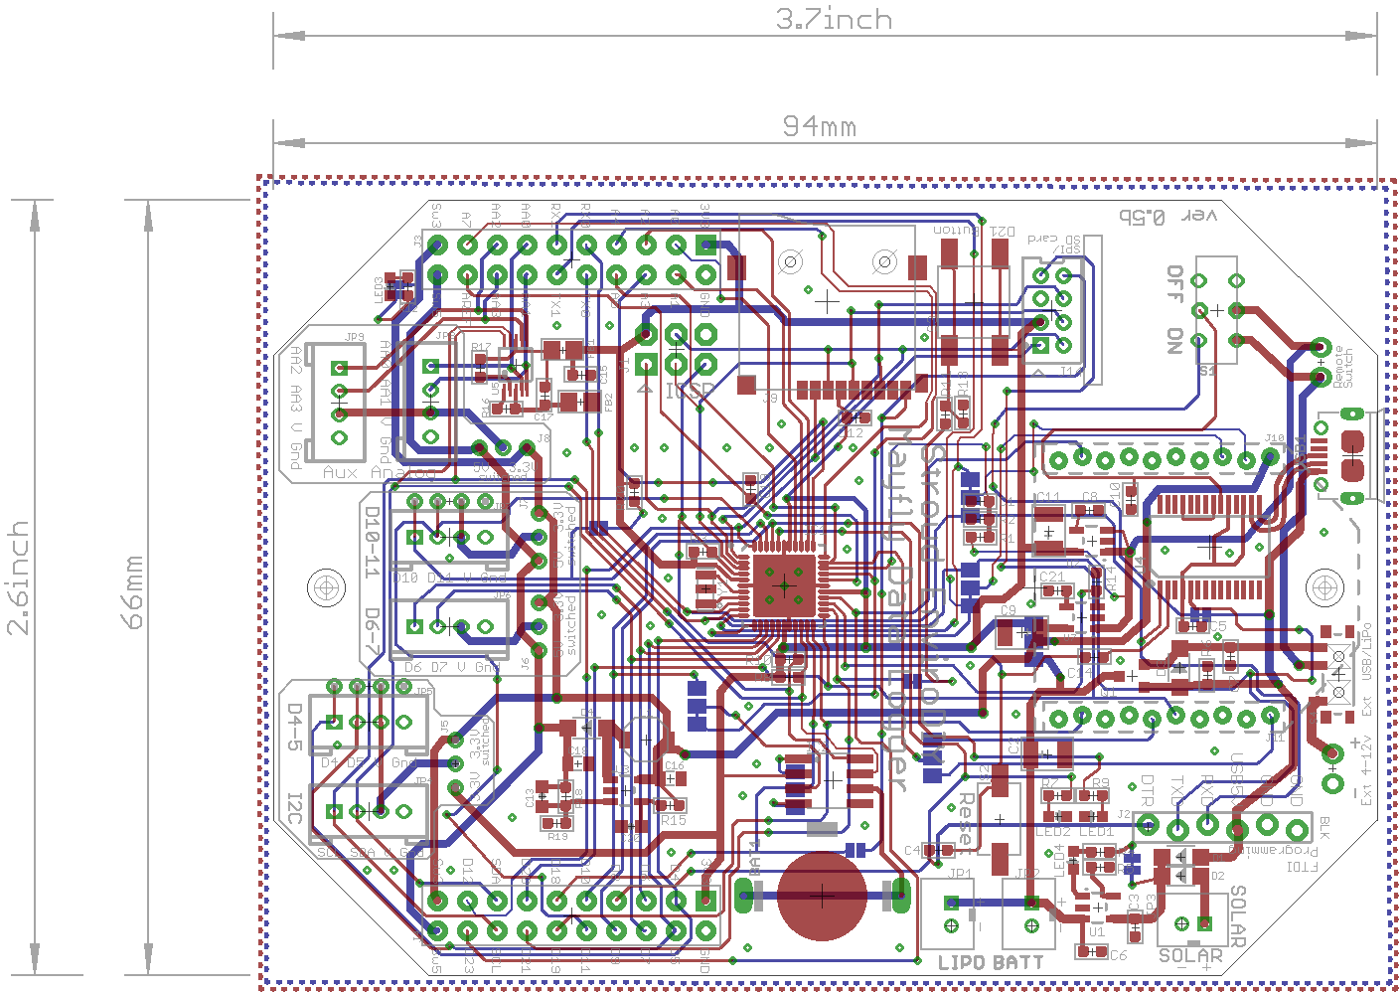
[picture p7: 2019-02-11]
hardware/Mayfly_v0p5b/Mayfly_0p5b_img.png

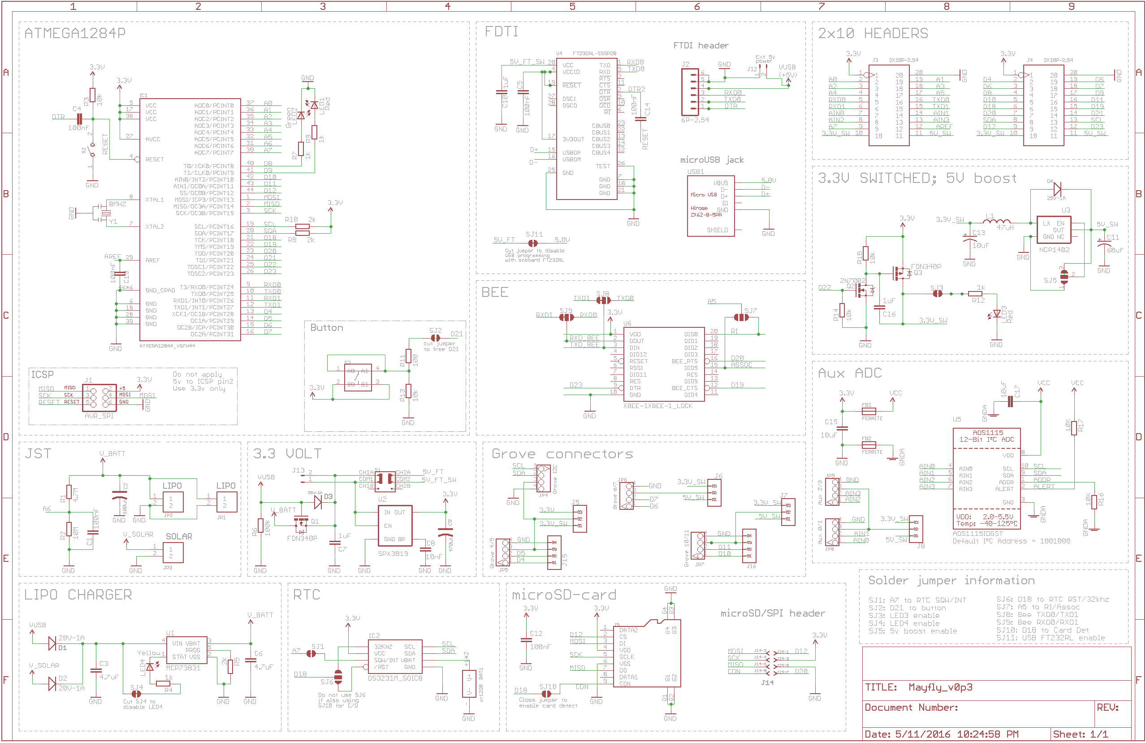
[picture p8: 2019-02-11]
hardware/Mayfly_v0p3/mayfly_v0p3_schematic.png

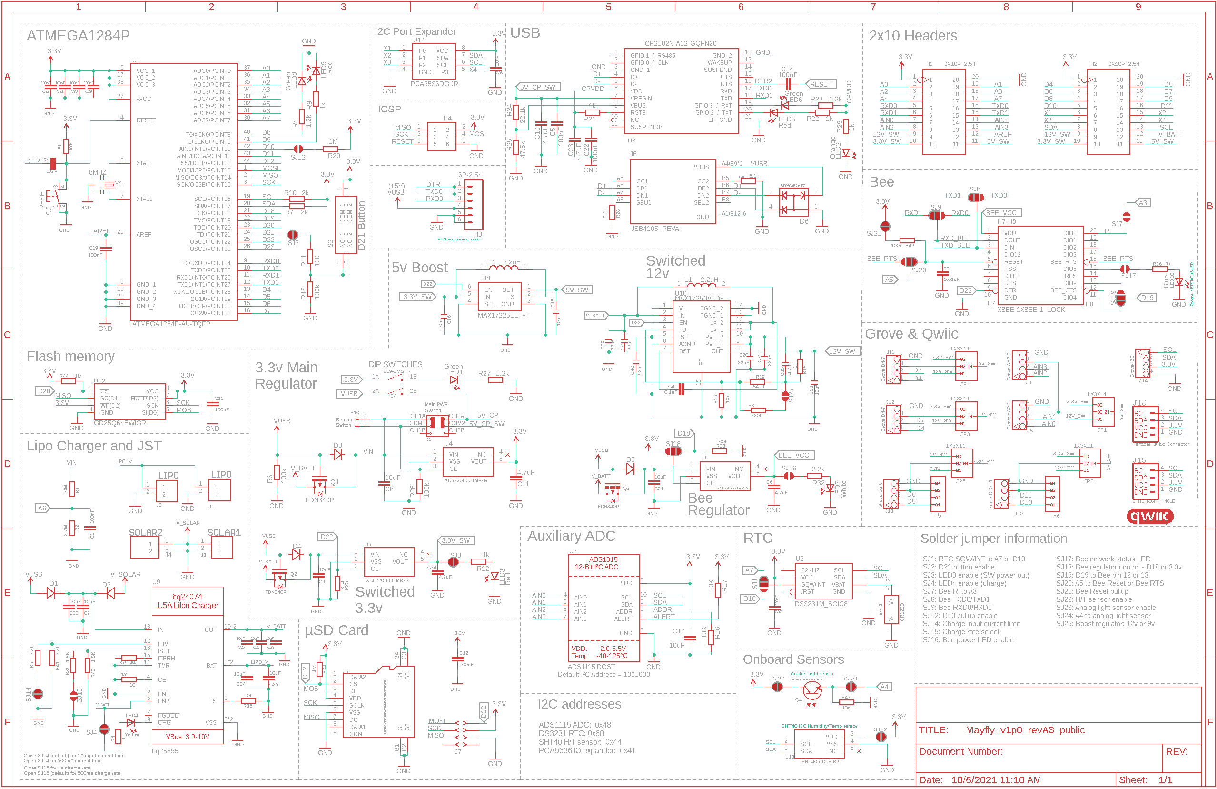
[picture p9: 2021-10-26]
hardware/Mayfly_v1p0/Mayfly_v1p0_revA3_public.png

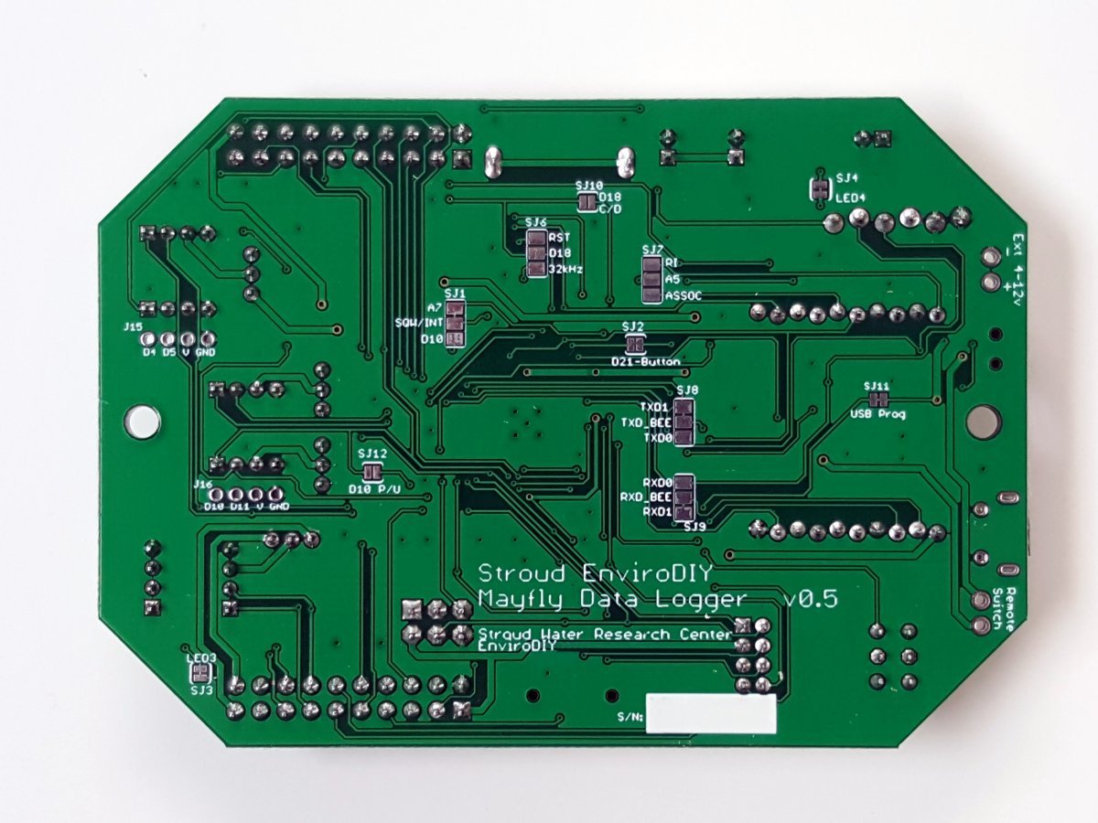
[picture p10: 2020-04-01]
doc/images/mayfly0.5_bottomview.jpg

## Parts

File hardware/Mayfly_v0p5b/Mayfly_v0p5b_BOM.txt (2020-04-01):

Partlist exported from /Users/fisher/Downloads/Mayfly_v0p5b/Mayfly_v0p5b.sch at 6/5/19 5:30 PM

Part Value                            Device                                     Package                          Description                                                                             MPN                PROD_ID  VALUE         
BAT1 cr1220                           DIP-BATTERY-CELL-HOLDER(1220)              BAT2P-13.5-CR1220                320170002                                                                                                           cr1220        
C1   100nF                            C_0603                                     C0603                                                                                                                                                              
C2   100uf                            TANTALUM-SMD-100UF-10V(AVX-B)              AVX-B                            302020015                                                                               TAJB107M010#NJ              100uf         
C3   4.7uF                            C_0603                                     C0603                                                                                                                                                              
C4   100nF                            C_0603                                     C0603                                                                                                                                                              
C5   100nF                            C_0603                                     C0603                                                                                                                                                              
C6   4.7uF                            C_0603                                     C0603                                                                                                                                                              
C7   1uF                              C_0603                                     C0603                                                                                                                                                              
C8   10nF                             C_0603                                     C0603                                                                                                                                                              
C9   100uf                            TANTALUM-SMD-100UF-10V(AVX-B)              AVX-B                            302020015                                                                               TAJB107M010#NJ              100uf         
C10  1uF                              C_0603                                     C0603                                                                                                                                                              
C11  100uf                            TANTALUM-SMD-100UF-10V(AVX-B)              AVX-B                            302020015                                                                               TAJB107M010#NJ              100uf         
C12  100nF                            C_0603                                     C0603                                                                                                                                                              
C13  10pf                             CAP0603-CAP                                0603-CAP                         Capacitor                                                                                                                         
C14  100nF                            C_0603                                     C0603                                                                                                                                                              
C15  10uF                             C_0603                                     C0603                                                                                                                                                              
C16  4.7uF                            CAP0805                                    0805                             Capacitor                                                                                                                         
C17  10uF                             C_0603                                     C0603                                                                                                                                                              
C18  10uF                             CAP0805                                    0805                             Capacitor                                                                                                                         
C19  100nF                            C_0603                                     C0603                                                                                                                                                              
C20  56nf                             CAP0603-CAP                                0603-CAP                         Capacitor                                                                                                                         
C21  10nF                             C_0603                                     C0603                                                                                                                                                              
D1   20V-1A                           SMD-DIODE-SCHOTTKY-20V-1A(SOD-123)         SOD-123                          304020034                                                                               B5819W                      20V-1A        
D2   20V-1A                           SMD-DIODE-SCHOTTKY-20V-1A(SOD-123)         SOD-123                          304020034                                                                               B5819W                      20V-1A        
D3   20V-1A                           SMD-DIODE-SCHOTTKY-20V-1A(SOD-123)         SOD-123                          304020034                                                                               B5819W                      20V-1A        
D4   20V-1A                           SMD-DIODE-SCHOTTKY-20V-1A(SOD-123)         SOD-123                          304020034                                                                               B5819W                      20V-1A        
FB1  FERRITE                          FERRITE0805                                0805                             Ferrite Bead                                                                                                                      
FB2  FERRITE                          FERRITE0805                                0805                             Ferrite Bead                                                                                                                      
IC1  ATMEGA1284P_VQFN44               ATMEGA1284P_VQFN44                         VQFN44                                                                                                                                                             
IC2  DS3231M_SOIC8                    DS3231M_SOIC8                              SO8                                                                                                                                                                
J1   AVR_SPI                          AVR_SPI_PRG_6NS                            2X3-NS                           AVR ISP 6 Pin                                                                                                                     
J2   6P-2.54                          M06FEMALE_LOCK                             1X06_FEMALE_LOCK.010             Header 6                                                                                                                          
J3   2X10P-2.54                       DIP-BLACK-FEMALE-HEADER(2X10P-2.54)-2.54   H2X10-2.54                       320030090                                                                               F185-1210A0BA1              2X10P-2.54    
J4   2X10P-2.54                       DIP-BLACK-FEMALE-HEADER(2X10P-2.54)-2.54   H2X10-2.54                       320030090                                                                               F185-1210A0BA1              2X10P-2.54    
J5   1X3                              1X3                                        1X3                                                                                                                                                                
J6   1X3                              1X3                                        1X3                                                                                                                                                                
J7   1X3                              1X3                                        1X3                                                                                                                                                                
J8   1X3                              1X3                                        1X3                                                                                                                                                                
J9   MICRO-SDCARD-CONNECTOR-3300060P1 MICRO-SDCARD-CONNECTOR-3300060P1           9P-SMD-W-RING                    Micro SD Card                                                                                                                     
J12  JUMPER-PTH-2-NO                  JUMPER-PTH-2-NO                            PTH-JUMPER-2-NO_NO_SILK                                                                                                                                            
J13  JUMPER-PTH-2-NO                  JUMPER-PTH-2-NO                            PTH-JUMPER-2-NO_NO_SILK                                                                                                                                            
J14  79107-08_S                       79107-08_S                                 79107-08                         RECEPTACAL                                                                                                                        
J15  1X4                              1X4                                        1X4                                                                                                                                                                
J16  1X4                              1X4                                        1X4                                                                                                                                                                
JP1  JST_EPH_2PIN                     JST_EPH_2PIN                               JST_EPH_B2B-PH-K-S                                                                                                                                                 
JP2  JST_EPH_2PIN                     JST_EPH_2PIN                               JST_EPH_B2B-PH-K-S                                                                                                                                                 
JP3  JST_EPH_2PIN                     JST_EPH_2PIN                               JST_EPH_B2B-PH-K-S                                                                                                                                                 
JP4  Grove I2C                        GROVE-CONNECTOR-DIP(4P-2.0)                HW4-2.0                          320110033                                                                                                           4P-2.0        
JP5  4P-2.0                           GROVE-CONNECTOR-DIP(4P-2.0)                HW4-2.0                          320110033                                                                                                           4P-2.0        
JP6  Grove 6/7                        GROVE-CONNECTOR-DIP(4P-2.0)                HW4-2.0                          320110033                                                                                                           4P-2.0        
JP7  4P-2.0                           GROVE-CONNECTOR-DIP(4P-2.0)                HW4-2.0                          320110033                                                                                                           4P-2.0        
JP8  4P-2.0                           GROVE-CONNECTOR-DIP(4P-2.0)                HW4-2.0                          320110033                                                                                                           4P-2.0        
JP9  4P-2.0                           GROVE-CONNECTOR-DIP(4P-2.0)                HW4-2.0                          320110033                                                                                                           4P-2.0        
L1   1.5uH                            INDUCTORVLF4012A                           VLF4012A                         Inductors                                                                                                                         
LED1 Red                              LED0603                                    LED-0603                         LEDs                                                                                                                              
LED2 Green                            LED0603                                    LED-0603                         LEDs                                                                                                                              
LED3 Red                              LED0603                                    LED-0603                         LEDs                                                                                                                              
LED4 Yellow                           LED0603                                    LED-0603                         LEDs                                                                                                                              
Q1   FDN340P                          MOSFET-P-CHANNELSMALL                      SOT23-S-PADS                                                                                                                                                       
R1   10M                              R_0603                                     R0603                                                                                                                                                              
R2   2.7M                             R_0603                                     R0603                                                                                                                                                              
R3   10k                              R_0603                                     R0603                                                                                                                                                              
R4   1k                               R_0603                                     R0603                                                                                                                                                              
R5   2k                               R_0603                                     R0603                                                                                                                                                              
R6   100k                             R_0603                                     R0603                                                                                                                                                              
R7   220                              R_0603                                     R0603                                                                                                                                                              
R8   2k                               R_0603                                     R0603                                                                                                                                                              
R9   1k                               R_0603                                     R0603                                                                                                                                                              
R10  2k                               R_0603                                     R0603                                                                                                                                                              
R11  100                              R_0603                                     R0603                                                                                                                                                              
R12  1k                               R_0603                                     R0603                                                                                                                                                              
R13  10k                              R_0603                                     R0603                                                                                                                                                              
R14  100k                             R_0603                                     R0603                                                                                                                                                              
R15  10k                              R_0603                                     R0603                                                                                                                                                              
R16  10K                              R_0603                                     R0603                                                                                                                                                              
R17  10K                              R_0603                                     R0603                                                                                                                                                              
R18  30.1k                            R_0603                                     R0603                                                                                                                                                              
R19  10k                              R_0603                                     R0603                                                                                                                                                              
R20  1M                               R_0603                                     R0603                                                                                                                                                              
S1   SWITCH-2CH-6P-3010010P1          SWITCH-2CH-6P-3010010P1                    6P-2CH-2.54-9.1X3.5X3.2+2H       MS-22D18 G2 ROHS                                                                                                                  
S2                                    SMD-BUTTON(2P-6.0X3.0X2.5MM)-DHT-1163S     SW2-4.0-6.0X3.0X2.5MM            311020029                                                                                                                         
S3                                    SMD-SWITCH-TACTILE-SPST-NO(4P-D6.0MM)      SW4-SMD-6.0X6.0X5.0MM            311020004                                                                               DTSM-62K-S-V-T/R                          
S4                                    SWITCH-SPDT-SMD-A                          SWITCH-SPST-SMD-A                SPDT Switch                                                                                                                       
SJ1                                   SOLDERJUMPER_2WAYT                         SJ_2                             Solder Jumper                                                                                                                     
SJ2  SOLDERJUMPERNO                   SOLDERJUMPERNO                             SJ_2S-NO                         Solder Jumper                                                                                                                     
SJ3  SOLDERJUMPERNO                   SOLDERJUMPERNO                             SJ_2S-NO                         Solder Jumper                                                                                                                     
SJ4  SOLDERJUMPER_NC                  SOLDERJUMPER_NC                            SJ_2S_NC                                                                                                                                                           
SJ6                                   SOLDERJUMPER_2WAYT                         SJ_2                             Solder Jumper                                                                                                                     
SJ7                                   SOLDERJUMPER_2WAYT                         SJ_2                             Solder Jumper                                                                                                                     
SJ8  SJ_3WAY_12SHORT                  SJ_3WAY_12SHORT                            SJ_3WAY_12SHORT                                                                                                                                                    
SJ9  SJ_3WAY_12SHORT                  SJ_3WAY_12SHORT                            SJ_3WAY_12SHORT                                                                                                                                                    
SJ10 SOLDERJUMPERNO                   SOLDERJUMPERNO                             SJ_2S-NO                         Solder Jumper                                                                                                                     
SJ11 JUMPER-PAD-2-NC_BY_TRACENO_SILK  JUMPER-PAD-2-NC_BY_TRACENO_SILK            PAD-JUMPER-2-NC_BY_TRACE_NO_SILK                                                                                                                                   
SJ12 SOLDERJUMPERNO                   SOLDERJUMPERNO                             SJ_2S-NO                         Solder Jumper                                                                                                                     
SJ13 SJ_3WAY_12SHORT                  SJ_3WAY_12SHORT                            SJ_3WAY_12SHORT                                                                                                                                                    
U1   MCP73831                         MCP73831                                   SOT23-5                          Miniature single cell, fully integrated Li-Ion, Li-polymer charge management controller                    IC-09995               
U2   SPX3819                          V_REG_LDOSMD                               SOT23-5                          Voltage Regulator LDO                                                                                                             
U3   V_REG_SC4503                     V_REG_TPS61040SMD                          SOT23-5                                                                                                                                                            
U4   FT232RL-SSOP28                   INTERFACE-FT232RL(SSOP28)                  SSOP28-0.65-10.2X5.2MM           310070022                                                                               FT232RL                     FT232RL-SSOP28
U5   ADS1115IDGST                     ADC_ADS1015                                MSOP10                           ADS1015 - 12-bit 4-Channel I2C ADC with Internal PGA                                                                              
U6   XBEE-1XBEE-1_LOCK                XBEE-1XBEE-1_LOCK                          XBEE-1_LOCK                      Xbee module footprints                                                                                                            
U7   SPX3819                          V_REG_LDOSMD                               SOT23-5                          Voltage Regulator LDO                                                                                                             
USB1 ZX62-B-5PA                       MICRO-USB-SMD(ZX62-B-5PA)                  MICRO-USB5+6P-SMD-0.65-AB        320010005                                                                               ZX62-B-5PA                  ZX62-B-5PA    
Y1   8MHZ                             SMD-RESONATOR-8MHZ-33PF-0.1%(3P-3.2X1.3MM) X3-SMD-3.6X1.3X0.8MM             306030005                                                                               CSTCE8M00G15L99-R0          8MHZ

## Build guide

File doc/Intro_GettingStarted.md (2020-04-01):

Getting Started With the Mayfly Data Logger
==============

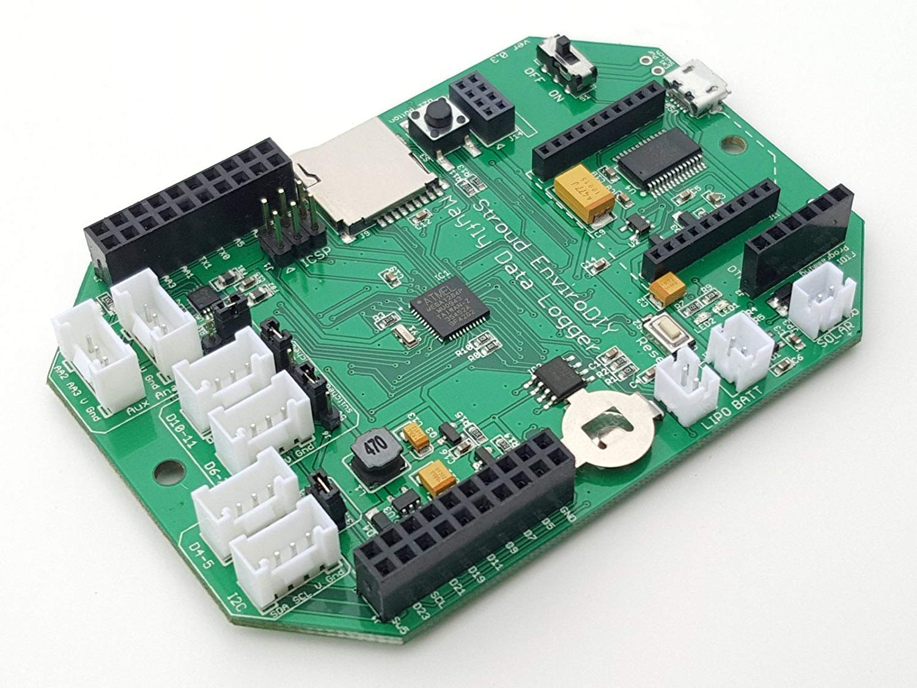
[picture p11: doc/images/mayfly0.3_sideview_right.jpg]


The EnviroDIY Mayfly Data Logger is a powerful, user-programmable microprocessor board that is fully compatible with the Arduino IDE software. It features the ATmega1284p processor, which is much more powerful than the 328p chip found on most other Arduino boards. It has 4 times more flash memory for sketches, 8 times more RAM, and almost twice as many input pins.

## Features:

* 128K Flash memory, 16K RAM
* 28 digital I/O pins, 8 analog pins, plus 4 additional high-resolution ADC pins
* 2 serial UART ports
* microSD memory card socket
* Onboard realtime clock (RTC) (DS3231)
* Solar lipo battery charging
* Bee module socket
* 2 LEDs, 1 user programmable push-button
* 3.3v main board voltage, additional 5-volt boost circuity for external devices
* Two 20-pin headers for accessing all available I/O pins
* 6 Grove-style sockets for easy connections to sensors and devices

The memory card socket, RTC, and solar charging features make it very easy to use this board for data logging and low-power operation. But it can also be used by itself, or with a wide variety of devices and accessories.
The Mayfly can be powered by a 3.7v lithium battery or through the microUSB port. Programming can be done through the microUSB port or via the FTDI header.

## Hardware Details

Find information about the Mayfly circuit board and its features, with descriptions about the various connectors and sockets, and the schematic diagram.

- [Get hardware details](https://github.com/EnviroDIY/EnviroDIY_Mayfly_Logger/tree/master/hardware).

## Software Instructions

Follow these instructions for adding the Mayfly board to your Arduino IDE, then you can program it with some of these sample code sketches.

- [Get software details](https://github.com/EnviroDIY/EnviroDIY_Mayfly_Logger/blob/master/doc/Software_Intro.md).

- Follow our [LearnEnviroDIY tutorial](https://envirodiy.github.io/LearnEnviroDIY/) to use our [ModularSensors](https://github.com/EnviroDIY/ModularSensors) code library and other [EnviroDIY libraries on GitHub](https://github.com/EnviroDIY)

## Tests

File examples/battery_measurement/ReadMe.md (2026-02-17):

Example: Battery Measurement on a Mayfly
==============

An example sketch showing how to measure the voltage of a lithium polymer (LiPo) battery connected to a Mayfly board.

### Background

On the Mayfly, analog pin **A6** is connected to a resistor divider that measures the voltage of the battery connected to the LiPo jack.
This example shows the theory behind measuring and calculating the battery voltage, so this concept can be used in other sketches that are battery powered.

NOTE:  If the USB cable or an FTDI adapter is connected to the Mayfly (ie, to connect to the Serial Monitor) the measured voltage will be from the voltage from USB/FTDI cable (~5V) and not the voltage of the LiPo battery.

### Tech Details

The Mayfly board operates at 3.3V - below the voltage of a healthy LiPo battery (3.5V - 4.2V) - meaning that the battery voltage cannot be measured directly.
To lower the voltage to a level the Mayfly can safely measure, we put two resisters in series and measure the voltage between them.
That is, we use a [voltage divider](https://en.wikipedia.org/wiki/Voltage_divider).
The formula (from Ohm's law) for the voltage measured across a voltage divider is:



If the resistors were exactly the same value, the measured voltage would be exactly half of the overall voltage.
On the newest versions of the Mayfly (v0.5, v0.5b, v1.0, and v1.1), the two resistors are set at 2.7MΩ and 10MΩ.
Adding those resistance values and solving for input voltage gives:



So for board versions v0.5 and v0.5b, use a multiplier of 4.7.  On the older Mayfly boards (v0.4 and v0.3) the two resistors were set at 4.7MΩ and 10MΩ leading to a multiplier of 1.47.

The resolution of the analog measurement on Mayfly pin A6 is 10 bit.
When reporting battery voltage, you should not report any further significant figures than the resolution of the measurement.

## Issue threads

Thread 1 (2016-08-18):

EnviroDIY/EnviroDIY_Mayfly_Logger #1: +5V boost efficiency mod

neilh10, 2016-08-18:
From v0.3 of mayfly schematic: If a hardware turn is made, I'm wondering could the +5V generation input L1/C13 be taken before the SPC3819 - ei D3/C7 (J13-2?)
The +5V boost enable of U3 EN could be tied to the 3.3VSW_EN (processor D22 Q2 gate)
This should have no functional impact, but should make the +5V boost circuit more efficient, and guarantee less likelihood of a power glitch on the 3.3V processor power line if a heavy load is present for 3.3V_SW_EN

s-hicks2, 2016-11-29:
Yes, it would be better if the supply for the NCP1402 was on the battery side of the SPX3819 3.3v regulator, however precautions would need to be taken to ensure that the NCP1402 doesn't see more than 6v input, which is why we opted to use the regulated supply instead.  Now that the NCP1402 has been obsoleted, future versions will have a completely different boost circuit.

closed 2016-11-29 by s-hicks2

aufdenkampe, 2018-02-01:
Mayfly v0.5, released in April 2017, has incorporated this feedback.
See https://envirodiy.org/features-of-the-new-mayfly-v0-5/

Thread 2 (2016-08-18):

EnviroDIY/EnviroDIY_Mayfly_Logger #2: +12V generation - NCP1403 opt

neilh10, 2016-08-18:
wrt Mayfly 0.3: If a turn of hardware is done, I wonder would it be possible to conside a layout where by the NCP1403 could be added - possibly as a user option in desoldering the NCP1402 +5V generation.
It seems like the NCP1403 could facilitate generation of  +12V with a reliable current of 20mA, even when the input voltage has dropped to  3.0V, 
The cost would be laying out the board with three optional components 2 resistors, 1cap (RFB1 RFB2 Cc in cct below). Possibly boosting the outcap rated voltage to +15V.
 This components would require one bypass strap to facilitate the current NCP1402-50T1 +5V 

[image]

This could support the large number of +12V sensors, both analog 4-20mA and also with the addition of a RS485 interface the modbus sensors.

s-hicks2, 2016-11-29:
We thought about incorporating a 12v boost option, but since very few end users would actually need it, we decided to leave it off.  We figured it would be easier to generate other voltage on a separate shield or breakout board since it would also require other circuitry like level shifting for the logic and whatever other requirements their signals would need.  But perhaps there's a way to make the layout more modifiable on the next version for people who want to swap out the boost regulator or add an additional one.

aufdenkampe, 2019-03-06:
For reference, neilh10 is referring to the [Modbus-Mafly-WingShield](https://github.com/EnviroDIY/SensorModbusMaster/tree/master/hardware/Modbus-Mayfly_WingShield), which can also easily boost to 9V or 12V.

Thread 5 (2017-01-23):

EnviroDIY/EnviroDIY_Mayfly_Logger #5: Modular Coding for Mayflies

aufdenkampe, 2017-01-23:
This is pasted from an email send by @fryarludwig to @SRGDamia1 about the [SimpleLoggingExample](https://github.com/EnviroDIY/EnviroDIY_Mayfly_Logger/tree/SimpleLoggingExample) and [Modular-Code-Example](https://github.com/EnviroDIY/EnviroDIY_Mayfly_Logger/tree/Modular-Code-Example) feature branches in this repo:

> I've revisited the modular code example, and my original plan for adding multiple values to single sensors would be the wrong approach. A better approach would be more time consuming and would change the current relationship between "sensors" and "dataValues" - I can see this being useful for long-term goals, but is not necessary for the workshop.
> 
> I imagine the SimpleLoggingExample would give you the best results for time committed, given your sensor requirements. This is a single-file example we put together to allow users more control while limiting inherent complexity at the same time.
> 
> To help get you started in the EnviroDIY_Mayfly_Logger.ino file:
> line 37: The config.h file was moved to here - change as needed
> line 74: We have a global sensor variable. Add the variables for the values you want to collect here, and feel free to get rid of the onboard_temperature value.
> line 238: This is the function you'll use to update the variables you created above. Feel free to add a sensor's wake/sleep functions inside this, or you can add those on line 280.
> line 252: Generate your JSON string here for the POST request.
> line 267: This is where we set the time. You mentioned you sync this with the computer, so remove or replace as needed.

aufdenkampe, 2017-01-23:
Once the dust has settled on this sprint, if we start thinking about modularizing the code, we might wan to take a look at the Arduino code here [https://github.com/NorthernWidget/Logger ](https://github.com/NorthernWidget/Logger ). Shannon and I have know the lead developer of that repo, Andy Wickert, for years, and he reached out to us at AGU and in early January about collaborating on a single, modular codebase for Arduino-compatible environmental data loggers.  Andy is that the University of Minnesota, so I'll probably meet with Andy sometime in the next few weeks.

aufdenkampe, 2017-02-20:
@SRGDamia1 just started this effort: https://github.com/EnviroDIY/ModularSensors

SRGDamia1, 2018-09-19:
I think this can safely be closed.

closed 2018-09-19 by SRGDamia1

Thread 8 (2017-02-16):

EnviroDIY/EnviroDIY_Mayfly_Logger #8: GPRSBee class error on "logging_to_EnviroDIY.ino"

aufdenkampe, 2017-02-16:
@SRGDamia1, yesterday 4 of us at LimnoTech tried out https://github.com/EnviroDIY/EnviroDIY_Mayfly_Logger/blob/master/examples/logging_to_EnviroDIY/logging_to_EnviroDIY.ino by making modifications in separate personal branches.

Unfortunately, I couldn't get the sketch to Verify, even though I have my libraries updated to the most recent. On my two different laptops (both macOS 10.12.3), I got a `'class GPRSbeeClass' has no member named 'addHTTPHeaders'` error on line 477. However my 3 colleagues, all running windows, had no problem verifying their sketches and now one is logging to Data.EnviroDIY.org.

Here is the full error:

```
Arduino: 1.8.0 (Mac OS X), Board: "EnviroDIY Mayfly 1284p"

/Users/aaufdenkampe/Documents/Arduino/EnviroDIY_Mayfly_Logger/examples/logging_to_EnviroDIY/logging_to_EnviroDIY.ino: In function 'int postDataGPRS(bool)':
logging_to_EnviroDIY:477: error: 'class GPRSbeeClass' has no member named 'addHTTPHeaders'
     gprsbee.addHTTPHeaders(header);
             ^
logging_to_EnviroDIY:478: error: 'class GPRSbeeClass' has no member named 'addContentType'
     gprsbee.addContentType(F("application/json"));
             ^
Multiple libraries were found for "SD.h"
 Used: /Users/aaufdenkampe/Documents/Arduino/libraries/SD
 Not used: /Applications/Arduino.app/Contents/Java/libraries/SD
exit status 1
'class GPRSbeeClass' has no member named 'addHTTPHeaders'

This report would have more information with
"Show verbose output during compilation"
option enabled in File -> Preferences.
```

Any ideas?

SRGDamia1, 2017-02-16:
It really looks like your library is not up to date.  Given you're also getting an error with finding double libraries for SD.h (which is a built-in that I didn't touch), I think there might be something goofy going on with how your software is finding your libraries.  Are you sure you restarted the IDE after updating?  You definitely did not update the library with the IDE by recloned from git, right?  Can you post the verbose output?

SRGDamia1, 2018-09-19:
This example should just be removed; it's pretty "ancient."

brianjastram, 2019-02-22:
I'm getting a similar GPRSBee error at the end of the below copied verbose report.
I just tried the BPRSbee-master library I extracted from https://github.com/SodaqMoja/GPRSbee.
Can you tell what I'm missing?

Arduino: 1.8.8 (Windows 7), Board: "EnviroDIY Mayfly 1284p"

C:\Program Files (x86)\Arduino\arduino-builder -dump-prefs -logger=machine -hardware C:\Program Files (x86)\Arduino\hardware -hardware C:\Users\brian.jastram\AppData\Local\Arduino15\packages -tools C:\Program Files (x86)\Arduino\tools-builder -tools C:\Program Files (x86)\Arduino\hardware\tools\avr -tools C:\Users\brian.jastram\AppData\Local\Arduino15\packages -built-in-libraries C:\Program Files (x86)\Arduino\libraries -libraries U:\My Documents\Arduino\libraries -fqbn=EnviroDIY:avr:envirodiy_mayfly -ide-version=10808 -build-path C:\Users\BRIAN~1.JAS\AppData\Local\Temp\arduino_build_637140 -warnings=none -build-cache C:\Users\BRIAN~1.JAS\AppData\Local\Temp\arduino_cache_574906 -prefs=build.warn_data_percentage=75 -prefs=runtime.tools.avr-gcc.path=C:\Program Files (x86)\Arduino\hardware\tools\avr -prefs=runtime.tools.avr-gcc-4.8.1-arduino5.path=C:\Users\brian.jastram\AppData\Local\Arduino15\packages\arduino\tools\avr-gcc\4.8.1-arduino5 -prefs=runtime.tools.avrdude.path=C:\Program Files (x86)\Arduino\hardware\tools\avr -prefs=runtime.tools.avrdude-6.0.1-arduino5.path=C:\Users\brian.jastram\AppData\Local\Arduino15\packages\arduino\tools\avrdude\6.0.1-arduino5 -prefs=runtime.tools.avr-gcc-5.4.0-atmel3.6.1-arduino2.path=C:\Program Files (x86)\Arduino\hardware\tools\avr -prefs=runtime.tools.arduinoOTA.path=C:\Program Files (x86)\Arduino\hardware\tools\avr -prefs=runtime.tools.arduinoOTA-1.2.1.path=C:\Program Files (x86)\Arduino\hardware\tools\avr -prefs=runtime.tools.avrdude-6.3.0-arduino14.path=C:\Program Files (x86)\Arduino\hardware\tools\avr -verbose U:\My Documents\Arduino\Sketches\EnviroDIY_Mayfly_Logger_Feb22\EnviroDIY_Mayfly_Logger_Feb22.ino
C:\Program Files (x86)\Arduino\arduino-builder -compile -logger=machine -hardware C:\Program Files (x86)\Arduino\hardware -hardware C:\Users\brian.jastram\AppData\Local\Arduino15\packages -tools C:\Program Files (x86)\Arduino\tools-builder -tools C:\Program Files (x86)\Arduino\hardware\tools\avr -tools C:\Users\brian.jastram\AppData\Local\Arduino15\packages -built-in-libraries C:\Program Files (x86)\Arduino\libraries -libraries U:\My Documents\Arduino\libraries -fqbn=EnviroDIY:avr:envirodiy_mayfly -ide-version=10808 -build-path C:\Users\BRIAN~1.JAS\AppData\Local\Temp\arduino_build_637140 -warnings=none -build-cache C:\Users\BRIAN~1.JAS\AppData\Local\Temp\arduino_cache_574906 -prefs=build.warn_data_percentage=75 -prefs=runtime.tools.avr-gcc.path=C:\Program Files (x86)\Arduino\hardware\tools\avr -prefs=runtime.tools.avr-gcc-4.8.1-arduino5.path=C:\Users\brian.jastram\AppData\Local\Arduino15\packages\arduino\tools\avr-gcc\4.8.1-arduino5 -prefs=runtime.tools.avrdude.path=C:\Program Files (x86)\Arduino\hardware\tools\avr -prefs=runtime.tools.avrdude-6.0.1-arduino5.path=C:\Users\brian.jastram\AppData\Local\Arduino15\packages\arduino\tools\avrdude\6.0.1-arduino5 -prefs=runtime.tools.avr-gcc-5.4.0-atmel3.6.1-arduino2.path=C:\Program Files (x86)\Arduino\hardware\tools\avr -prefs=runtime.tools.arduinoOTA.path=C:\Program Files (x86)\Arduino\hardware\tools\avr -prefs=runtime.tools.arduinoOTA-1.2.1.path=C:\Program Files (x86)\Arduino\hardware\tools\avr -prefs=runtime.tools.avrdude-6.3.0-arduino14.path=C:\Program Files (x86)\Arduino\hardware\tools\avr -verbose U:\My Documents\Arduino\Sketches\EnviroDIY_Mayfly_Logger_Feb22\EnviroDIY_Mayfly_Logger_Feb22.ino
Using board 'envirodiy_mayfly' from platform in folder: C:\Users\brian.jastram\AppData\Local\Arduino15\packages\EnviroDIY\hardware\avr\1.0.0
Using core 'arduino' from platform in folder: C:\Program Files (x86)\Arduino\hardware\arduino\avr
Detecting libraries used...
"C:\\Program Files (x86)\\Arduino\\hardware\\tools\\avr/bin/avr-g++" -c -g -Os -w -std=gnu++11 -fpermissive -fno-exceptions -ffunction-sections -fdata-sections -fno-threadsafe-statics -Wno-error=narrowing -flto -w -x c++ -E -CC -mmcu=atmega1284p -DF_CPU=8000000L -DARDUINO=10808 -DARDUINO_AVR_ENVIRODIY_MAYFLY -DARDUINO_ARCH_AVR "-IC:\\Program Files (x86)\\Arduino\\hardware\\arduino\\avr\\cores\\arduino" "-IC:\\Users\\brian.jastram\\AppData\\Local\\Arduino15\\packages\\EnviroDIY\\hardware\\avr\\1.0.0\\variants\\mayfly" "C:\\Users\\BRIAN~1.JAS\\AppData\\Local\\Temp\\arduino_build_637140\\sketch\\EnviroDIY_Mayfly_Logger_Feb22.ino.cpp" -o nul
"C:\\Program Files (x86)\\Arduino\\hardware\\tools\\avr/bin/avr-g++" -c -g -Os -w -std=gnu++11 -fpermissive -fno-exceptions -ffunction-sections -fdata-sections -fno-threadsafe-statics -Wno-error=narrowing -flto -w -x c++ -E -CC -mmcu=atmega1284p -DF_CPU=8000000L -DARDUINO=10808 -DARDUINO_AVR_ENVIRODIY_MAYFLY -DARDUINO_ARCH_AVR "-IC:\\Program Files (x86)\\Arduino\\hardware\\arduino\\avr\\cores\\arduino" "-IC:\\Users\\brian.jastram\\AppData\\Local\\Arduino15\\packages\\EnviroDIY\\hardware\\avr\\1.0.0\\variants\\mayfly" "-IC:\\Program Files (x86)\\Arduino\\hardware\\arduino\\avr\\libraries\\Wire\\src" "C:\\Users\\BRIAN~1.JAS\\AppData\\Local\\Temp\\arduino_build_637140\\sketch\\EnviroDIY_Mayfly_Logger_Feb22.ino.cpp" -o nul
"C:\\Program Files (x86)\\Arduino\\hardware\\tools\\avr/bin/avr-g++" -c -g -Os -w -std=gnu++11 -fpermissive -fno-exceptions -ffunction-sections -fdata-sections -fno-threadsafe-statics -Wno-error=narrowing -flto -w -x c++ -E -CC -mmcu=atmega1284p  [... cut ...]
Using library Sodaq_RTCTimer at version 1.0.0 in folder: U:\My Documents\Arduino\libraries\Sodaq_RTCTimer 
Using library EnviroDIY_DS3231 at version 1.3.2 in folder: U:\My Documents\Arduino\libraries\EnviroDIY_DS3231 
Using library EnviroDIY_PCInt_PCINT0 at version 1.2.1 in folder: U:\My Documents\Arduino\libraries\EnviroDIY_PCInt_PCINT0 
Using library GPRSbee-master at version 1.9.2 in folder: U:\My Documents\Arduino\libraries\GPRSbee-master 
exit status 1
'class GPRSbeeClass' has no member named 'addHTTPHeaders'

SRGDamia1, 2019-02-22:
Just to warn you, this example is NOT what I'd currently recommend using.  I would (strongly) suggest switching to the [ModularSensors ](https://github.com/EnviroDIY/ModularSensors) library to send data to enviroDIY.

To use this sketch you need to use branch v1.2_hacked of the EnviroDIY fork of the GPRSBee library:  https://github.com/EnviroDIY/GPRSbee/tree/v1.2_hacked.  That version was the last one to work properly on the Mayfly, and then was modified to allow the authentication headers needed to communicate with the EnviroDIY Data Portal.

SRGDamia1, 2019-02-22:
@brianjastram  If you're using the Arduino IDE, I would also recommend moving away from that in favor of PlatformIO

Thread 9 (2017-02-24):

EnviroDIY/EnviroDIY_Mayfly_Logger #9: Maxbotix sonar 0 mm readings between "good" readings, other delays

fisherba, 2017-02-24:
Using the sketch "mayfly_10_sonar.ino", the serial monitor gives several "0 mm" (and sometimes 9999 mm) readings between the correct distance readings. I noticed that the delay in the sketch doubled in an update yesterday (from 700 to 1400), and I hoped that would solve the issue for me, but I am still experiencing as many as 3-24 "0 mm" readings while the sketch runs. 

I am using Mayfly v0.3, and I wonder if the constant power for the D4-5 port could be part of the issue?

Also, it seems to take ~20-30 seconds to recognize a change in measured distance, meanwhile the old distance continues to output to the serial monitor (along with the 0 mm readings). Is this an expected behavior?

SRGDamia1, 2017-02-24:
I'm working on this right now over in the modular library (https://github.com/EnviroDIY/ModularSensors) but, in short, it's triply finickey.

1 - The sonar itself gives noisy readings, frequently spitting out 300 or 500 (around the blanking distances), and is just not terribly stable.  We're pretty sure this is just a fault of the sensor.  It also (by design) sends out 9999 or 4999 (depending on the model) when it cannot see a proper reflection because there's nothing close enough or there's too much noise in the reflections.

2 - On the Mayfly, you're reading the serial data from the sonar over a "software" serial port.  Faking a serial port with software is not nearly as solid and stable as a real hardware serial connection because it's all about baud and timing, etc.  So the software serial port implementation sometimes just misses or mangles the response from the sonar.  The sonar sends out several header lines and then the readings as "R####\r".  The code in the example is looking for that "R" character and then keeps the next 4 characters as numbers.  But it often gets confused because there are several R's in the header lines and the less-than-perfect serial connection frequently either misses or double-reads characters.  All of those responses get translated to 0.  I'm working on this part right now, but I don't have a good solution yet.  I put in some extra print statements to track it for debugging and had it working perfectly, but the very slight change in timing just from removing those print statements made it crash.

3 - Although the sonic has a very low power draw, according to @s-hicks2 when it starts up it somehow causes a glitch in the power on the board.  So if you're alternately turning on and cutting the power to the sonar with the D22 switched power pin, it can sometimes cause the whole board to reset or do weird things.  Because it does take such little power, you can power it with any of the other 3.3V or 5V digital pins on the board (ie, if you read off of 5 you can power with 4) and that isolates it from the shared power and reduces all the glitching.  If you're not turning the power on and off, though, this shouldn't be a problem.

fisherba, 2017-02-24:
Hi @SRGDamia1, the sketch at ModularSensors is working perfectly for me. That sketch is clearly turning the sensor on and off for readings (indicated by lights on board), but the workshop sketch doesn't do this. It seems to be constantly reading, which I understand is then recording all of the ill-timed information as "0 mm". I think updating the workshop sketch with the code from the modular set will be in our future. Thanks for the speedy reply.

SRGDamia1, 2017-02-24:
I've updated the MaxBotix part of the library (again).  I'm finally mostly satisfied with it now.

Just FYI, the red power LED only shows if the power is on to the "V" pins (controlled by #22).  If you have the sonar set so it's pulling power from another digital pin, there won't be any indicator whether it's on or off.  I've written the update functions for *all* of the sensors, though, so they first check that the sensor has power before trying to take a reading.  If you try to take a reading from a sensor using the modular library and you didn't power the sensor, it will automatically power the sensor, wait one second, take the reading, and then turn the power back off.  I'd still suggest separately turning the power on and off, though, if you're using more than one sensor so you can loop through the sensors a little faster and aren't flickering the power as much.

sgfulton, 2017-02-24:
To take a single serial reading, you need to power down or ground the trigger pin (4th pin from the right next to the signal pin).  To take a single reading, set the trigger pin HIGH for a delay of 1 millisecond, and then set LOW again.  The system will send an R####<13> (/R or carriage return).  To read the serial input buffer, strip out the R and the /R and convert to integer or float.  That reading is in mm.

We have found that taking one second readings for 30 seconds, then averaging the resulting 30-sec median value over 5 minutes gives results that vary about 0.5 cm.

This is only true if a filter is added to the sensor.  For our sensor (MaxBotix MB7383 Outdoor Ultrasonic Sensor), we soldered a 100 uF electrolitic capacitor between the ground and Vin pin on the MaxBotix, and then a 10 ohm resistor to the + side of the electrolitic capacitor.  The 22 gauge 4-wire shielded cable was attached to these leads.  

The system worked equally well with hardware serial on an Arduino Mega and software serial.

SRGDamia1, 2017-02-24:
@s-hicks2, what do you think?  I like @sgfulton 's way of interfacing with the sensor, but we'd need to re-solder the grove connections.

s-hicks2, 2017-02-25:
Sara, the Grove connector on the ultrasonic sensor you're using was only 
intended for use during the constanly-powered workshop example sketch.  
For actual real-world deployments, I put a screw terminal block on the 
ultrasonic sensor so that the end-user can easily connect wires to 
whatever pins they want.

I use the sensors in the free-running mode by letting the trigger pin 
float.  I experimented with external capacitor filters awhile back but 
didn't see much improvement, and after discussions with the techs at 
Maxbotix, we determined that it wasn't necessary.

For our deployments, there usually isn't any variation between readings 
that are made in quick succession.  I can take 1 reading or 20 in a row, 
and might only see 1 or 2 mm of variation.  So I don't average the 
readings for very long in order to minimize the time that the logger is 
awake. Where we see the greater problem in the range readings is cause 
by temperature variations between subsequent sample periods.  If the 
sensor housing or air has even moderate temperature changes, that will 
be evident in a change in distance reading on the order of several 
millimeters.  We use the an external temperature sensor connected to pin 
1 of the ultrasonic sensor (and mounted to an external, shaded location) 
to provide a more accurate compensation for the offset problems caused 
by the air/sensor housing temperature change.

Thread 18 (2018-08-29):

EnviroDIY/EnviroDIY_Mayfly_Logger #18: PWM ports

WeatherNut, 2018-08-29:
I have recently been trying to connect multiple analog sensors to the mayfly board using a 16-channel analog multiplexer. I have reached a little hurdle however. The PWM ports are clearly labeled on the arduino uno boards, while the mayfly they are not. Does anyone now which digital ports are PWM ports?

SRGDamia1, 2018-08-29:
Should be pins D4, D5, (Timer 1 - 16 bit) D6, D7, (Timer 2 - 8 bit) D11, D12, (Timer 0 - 8 bit) D14, D15 (Timer 3, 16 bit).

closed 2018-08-29 by SRGDamia1

aufdenkampe, 2018-08-30:
@WeatherNut, the Mayfly is built on the [ATmega1284p](http://ww1.microchip.com/downloads/en/DeviceDoc/doc8059.pdf) chip, so digging into those specs is an important place to start.

Then, to translate to the numbering scheme printed on the Mayfly, you'll need to look at the Mayfly schematics here: https://github.com/EnviroDIY/EnviroDIY_Mayfly_Logger/tree/master/hardware

@SRGDamia1, was there an easier source of info for this than the 380 page [ATmega1284p](http://ww1.microchip.com/downloads/en/DeviceDoc/doc8059.pdf) spec sheet?

SRGDamia1, 2018-09-03:
Actually, the spec sheet wouldn't have told you which "Arduino" digital pin numbers could do PWM, only that all the OC pins from all timers were capable and which physical pins those were.  You need to look at the [pins_arduino.h](https://github.com/EnviroDIY/Arduino_boards/blob/master/envirodiyboards/variants/mayfly/pins_arduino.h) for the Mayfly to verify the assignment of the "Arduino" digital pin numbers to physical pins.  (They are not the same, and in fact the assignments on the Mayfly match the Mbili but are different from most other 1284p boards.)  The block with "digital_pin_to_timer_PGM" (line 208) its the actual assignment of physical timer pins to digital "Arduino" pins.

SRGDamia1, 2018-09-03:
The timer OC pins are also shown on the Mayfly schematic, along with their digital pin numbers:  https://raw.githubusercontent.com/EnviroDIY/EnviroDIY_Mayfly_Logger/master/hardware/mayfly_v0p5b_schematic.png

I don't know if there was ever another place where the PWM capable pins are specifically flagged.  I've never tried any pulse width modulation applications so I had to dig around a bit to figure out which pins could do it.

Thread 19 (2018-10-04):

### ISSUE TITLE
Mayfly_Logger PCB in Europe

### ISSUE THREAD

**Issue by dkalog** [EnviroDIY/EnviroDIY_Mayfly_Logger#19]
Hi ,

I am trying having access to MayFly Logger from some place in Europe either in NL or Greece. According to Amazon.com this is not possible. This leaves me with two options: a) either get the PCB from some place and solder the BOM myself on the PCB or b) getting the gerber/eagle  files and print them to PCB locally or c) the long way  going from the semantics --> PCB and then to the final product.  What do you suggest ?

**Comment by SRGDamia1** [comment]
I don't think there's currently any way direct way to get a Mayfly shipped anywhere except in the US.  The schematics are available, but the gerber/eagle files aren't and I doubt they'll ever be shared freely.  @s-hicks2 might know more.

While I think the Mayfly is quite nice, I would guess that it would be much, much easier for you to look into Mayfly alternatives than to try to manually solder something together.  The original Mayfly is very similar to the Sodaq Mbili.  Sodaq is based in the Netherlands, so I imagine you could get their products shipped to you.

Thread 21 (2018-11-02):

EnviroDIY/EnviroDIY_Mayfly_Logger #21: sleep mode current

neilh10, 2018-11-02:
Just checking on mA consumed during sleep - 
for the current 'develop' branch using logging_to_EnviroDIY.ino, on sleep the current reduces to about 3.5mA after EnviroDIYLogger.systemSleep() is executed. 
This is with a barebones Mayfly0.5b  and only one sensor ProcessorStats_SampleNumber()  in variableList[], no SD card, no Xbee or anything. Just the rtc coin battery added to the board.
I'm expecting to get to about 0.5mA as per  @s-hicks2  https://www.envirodiy.org/topic/low-power-project/
With Sensors sampling and Green and Red led its about 10.5mA

If I comment out the real work of sensor update - and just leave 
EnviroDIYLogger.checkInterval() - 
EnviroDIYLogger.systemSleep() 
then in one case it went to sleep and consumed 0.5mA - hurrah.

However on repeating the same exercise above, it didn't  reduce the current - but stayed at 3.5mA
So it could be that I just got lucky once - and it doesn't matter whether its actually running the sensors update or not.

I'm measuring current as taken for the LiIon battery with a good digital multimeter with a mA range (and also uA range). 
I've modified LiIon battery extension cable so that it works for a running mayfly.
I power up from cold by plugging in the LiIon cable
  
I can see EnviroDIYLogger.systemSleep() has a lot of good code to do a powerdown, but I'm not getting there. 

Just wondering if I'm missing a switch, or any suggestions on how to measure sleep current.  Thanks

SRGDamia1, 2018-11-02:
I've honestly never tested the sleep (or wake) current draw.

neilh10, 2018-11-02:
Thanks - just checking and putting it out there to see if anybody has any insights.
Its a difficult challenge as its like a leaky water line, so many place for current/uA to leak out.  
The Mayfly0.5 is a bit touchy on a longer battery cable and having a Digital Meter in the path - it was resetting - so needed to make the cable with a low impedance capacitor at the JP1/JP2 end.
There is a sketch that I can use to verify the base hardware and make sure that it is capable of getting that low - https://www.envirodiy.org/mayfly/software/sleeping-mayfly-logger-example/   
I seemed to get to 0.5mA once, so might be something like a floating input.  
There is a good structure of code to work with :).

SRGDamia1, 2018-11-02:
@aufdenkampe - want to send me one?

SRGDamia1, 2018-11-02:
Almost all of the work I've done to minimize power draw has been in working to minimize the sensor-on time.  The only "special" thing I have coded in to reduce the draw while actually sleeping is to force the I2C pins to go low in sleep to reduce parasitic draw.  On the processor, I'm disabling the on-board ADC, the brown-out detector, the various internal clocks, and going into "SLEEP_MODE_PWR_DOWN", which is the lowest power use setting.

neilh10, 2018-11-02:
I could write up a method for doing sleep power measurements.  
I think the goal needs to be clear and its a technically difficult challenging area . 
I would think the goal is that there is an easy  method to get good enough power for any release of software with some low cost (time and materials) methods.
Its technically challenging as there is a wide dynamic range of power demand and distributed  - the dynamic range is a technical problem.  That is when some Cellular modems are transmitting they can take 1000mA for short bursts. 
However for sleep measurements, need to be able to determine that the Mayfly power is about 0.5mA - or the measurement accuracy needs to be somewhere round +-/0.25mA (eg 0.1mA would be fine)
The problem is that this can only be quickly and accurately determined from the battery line.
If it is measured from the external line, then the LiPo needs to be disconnected so that it isn't taking current, and then I see the LiPo charger flashing LED4. I can experiment a bit more so if there is a stable condition with low quiescent for the LiPo charger +LED.
The MakerHawk UM25C USB Tester, looks to be excellent with at least a resolution of 0.1mA, but states its accuracy is 1%, which at 5.0000A is +-0.0500A or 50mA - so need to check if can actually measure accurately to at least 0.5mA.   It also looks to have a power accumulation register which would be good.
I have got a couple of lower cost USB testers and they only have a +/-10mA resolution.
I'll get a UM25C to try it.

For a LiPo cable current measurement if its of interest - it would be about having a Digital Voltmeter with 0.1mV resolution - and then a modified battery extension cable with a 0.1ohm in series most of the time. For a current pulse of 1A this would drop 100mV - which I think would be OK, but needs to be verified.
For sleep power measurements, a push button momentary switch would put in a 10 ohms resistor, and then a sleep current of 0.5mA would be 5mV.  Just a thought. I can could make up a few cables and distribute them if anybody is interested and has the Digital Voltmeter.

neilh10, 2018-11-03:
If I use the 
https://www.envirodiy.org/mayfly/software/sleeping-mayfly-logger-example/
and for platformIO I build against
https://github.com/EnviroDIY/Libraries.git#platformio
then when it sleeps I get 0.40mA. This is with a ScanDisk Ultra 16G inserted.
When its running, briefly writing to the SD card it peaks 7.9mA
I visually can't see the differences between sleeping-mayfly and logging_to_EnviroDIY.ino at this point, but I'm looking at it section by section.

neilh10, 2018-11-05:
I'm trying another approach that seems to be working , using a current monitor [Adafruit/904](https://www.adafruit.com/product/904) which has INA219B, with the I2C on a separate Mayfly board.
The results are verified with my Multimeter mA measurements.
The INA219B has 0.1mA resolution for series impedance of 0.01ohms, and a range +-400mA
In the picture the LiIon is +ve is connected to the INA219B, the Mayfly0.4#1 with the USB cable polls the I2C and reports current
The Mayfly0.5b#2 (with screwdriver & Xbee) has its power solely provided by the Rbat. The J2/FTDI monitoring cable has its power and DTR pins clipped so its only monitoring, and not providing power or causing a tty reset.
[image]

The Mayfly#1 running a modified
//https://github.com/adafruit/Adafruit_INA219/blob/master/examples/getcurrent/getcurrent.ino

With no Xbee, and Mayfly#2 running a simple program writing to the SD card every minute
https://www.envirodiy.org/mayfly/software/sleeping-mayfly-logger-example/

the results from Mayfly#1 are with polling about every 2seconds what you would expect - the multimeter reported 0.38mA - which the INA219B is limited to 0.1mA resolution with no rounding of measurements.

---Ina219(BUILD_TIMESTAMP 1541382006)
Reporting Power and current with INA219 0-400mA ...
mA:   0.30, V: 4.13, mW:    2
mA:   0.30, V: 4.11, mW:    2
mA:   0.30, V: 4.12, mW:    2
mA:   0.30, V: 4.12, mW:    2
mA:   0.30, V: 4.12, mW:    2
mA:   0.30, V: 4.12, mW:    2
mA:   0.30, V: 4.11, mW:    2
mA:   7.20, V: 4.11, mW:   29
mA:   0.30, V: 4.12, mW:    2
mA:   0.30, V: 4.12, mW:    2
mA:   0.30, V: 4.12, mW:    2
mA:   0.30, V: 4.12, mW:    2
mA:   0.30, V: 4.11, mW:    2
mA:   0.30, V: 4.11, mW:    2
mA:   0.30, V: 4.12, mW:    2
mA:   0.30, V: 4.11, mW:    2
mA:   0.30, V: 4.11, mW:    2
mA:   0.30, V: 4.11, mW:    2
mA:   0.30, V: 4.11, mW:    2
mA:   0.30, V: 4.11, mW:    2
mA:   0.30, V: 4.11, mW:    2
mA:   0.30, V: 4.12, mW:    2
mA:   0.30, V: 4.11, mW:    2
mA:   0.30, V: 4.11, mW:    2
mA:   0.30, V: 4.11, mW:    2
mA:   0.30, V: 4.11, mW:    2
mA:   0.30, V: 4.11, mW:    2
mA:   0.30, V: 4.11, mW:    2
mA:   0.30, V: 4.11, mW:    2
mA:   0.30, V: 4.11, mW:    2
mA:   0.30, V: 4.12, mW:    2
mA:   0.30, V: 4.11, mW:    2
mA:   0.30, V: 4.12, mW:    2
mA:   0.30, V: 4.12, mW:    2
mA:   0.30, V: 4.11, mW:    2
mA:   0.30, V: 4.12, mW:    2
mA:   0.30, V: 4.11, mW:    2
mA:   7.10, V: 4.11, mW:   29
mA:   0.30, V: 4.11, mW:    2
mA:   0.30, V: 4.11, mW:    2
mA:   0.30, V: 4.11, mW:    2
mA:   0.30, V: 4.12, mW:    2
mA:   0.30, V: 4.11, mW:    2
mA:   0.30, V: 4.12, mW:    2
-----
I have a spare adafruit.com/product/904  and cables so I could make up a similar setup tomorrow and share it...
I speculatively ordered/Digikey on Fri the following (hopefully arriving tomorrow) 
two 3650	INA219 FEATHERWING
one 2796	EVAL BRD FEATHER M0 ADALOGGER

aufdenkampe, 2018-11-05:
@neilh10, thanks for all these tests and ideas. I'll see what I can do to replicate your setup, and then we'll see if we can get @SRGDamia1 setup too.

SRGDamia1, 2018-11-06:
@aufdenkampe - I already have the feather M0, I'd just need the the featherwing and cables.

aufdenkampe, 2018-11-06:
@gcutrell, I think it would be really helpful to us to set up a high-frequency power recording system similar to the one that @neilh10 set up in his https://github.com/EnviroDIY/EnviroDIY_Mayfly_Logger/issues/21#issuecomment-435734443 above, which uses an [Adafruit INA219 High Side DC Current Sensor Breakout](https://www.adafruit.com/product/904) and an extra Mayfly. What do you think?

I know you've had success with the [MakerHawk UM25C USB Tester](https://www.amazon.com/MakerHawk-Bluetooth-Current-24-000V-Multimeter/dp/B07C9DQ4F9), but I think this might be able to provide a more accurate power readout for our purposes of figuring out what portions of the code are using the most power, because this enables us to configure the Mayfly exactly as we would for a field deployment.

neilh10, 2018-11-06:
Interesting find. It has three sensors - but turns out that the channels aren't as sensitive. 
The INA3221 1-LSB size for shunt voltage is +-40uV.  Actually mA measurement will depend on series shunt resistance and couldn't find that on their description, but nice to have resolution at about 0.1mA
For the sleep measurements, the 1LSB step size and Offset voltage are critical. The offset voltage determines how accurate it can measure 0.000V
The INA219B has 1-LSB +-10uV resolution, and also for low offset+/- 10uV offset - meaning that it would only error about 0.00000 by +-10uV.  
http://www.ti.com/lit/an/sboa194/sboa194.pdf compares the different TI devices. 
A board using  INA233 would be interesting as its sensitivity is 2.5uV and offset 2.5uV and contains a power Accumulator - ie can calc mAHrs - that would be useful to measure used mAHrs instead of just a digital sample at one point in time. 
The one other chip I've been keeping an eye on is Microchip PAC1720 dual (PAC1710 single) monitor,it is  low cost with voltage sense at 1LSB +-5uV. I have it designed in on a MKL27Z (cortex-M0) board - but not written a driver for it.

neilh10, 2018-11-28:
Great - would it work to make up battery cable so you can insert it inline with the battery?. I believe that is the easiest way of measuring sleep current.
Alternatively you can clip a battery cable's +V and insert it inline.
It also needs a groove 4wire cable.
https://github.com/neilh10/ModularSensors/wiki/Test-equipment-cable-monitor-LiIon
The code I've been using is on my branch "test_nh1"
https://github.com/neilh10/ModularSnsrsNh/tree/test_nh1/sensor_tests/Adafruit_INA219
I've also included it as a sensor (I keep meaning to clean it up and submit it) 

https://github.com/neilh10/ModularSensors/tree/work_nanolevel/examples/logging_to_EnviroDIY/lib/ModularSensors/src/sensors/TiIna291.h/cpp

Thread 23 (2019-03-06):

EnviroDIY/EnviroDIY_Mayfly_Logger #23: Upgrade solar charge controller.

aufdenkampe, 2019-03-06:
The Mayfly's Lipo battery solar charge controller chip ([MCP73831](https://www.microchip.com/wwwproducts/en/en024903#additional-features)) has a max output of 500 mA, which is about the 550 mA peak output of the [Voltaic's 3.5W solar panel](https://www.voltaicsystems.com/3-5-watt-panel) that we often use for our power-hungry sensors (i.e. YosemiTech turbidity with a brush) along with Adafruit's [2-cell 4400mAh](https://www.adafruit.com/product/354) or [3-cell 6600mAh](https://www.adafruit.com/product/353) Lithium Ion Battery Packs. This means that we can't increase the solar panel size beyond this for more power-hungry applications (such as several sensors with brushes).

It would be great to have a slightly higher rated and potentially more efficient charge controller. 

One option might be the [MCP73871](https://www.microchip.com/wwwproducts/en/en536670) controller that is used in the [Adafruit Solar Lithium Ion/Polymer charger - v2](https://www.adafruit.com/product/390) that can be modified to 1A charging and gets high marks in this review: https://www.voltaicsystems.com/blog/lithium-ion-charge-controller/.

Not sure if there are other pros/cons. Is there value at going with a MPPT (maximum power point tracker) charge controller?

everhamme, 2019-03-07:
Per most recommendations I've seen true MPTT is overkill and expensive.  Since our incoming voltage from solar is near 6V it's not too far off from the required charge voltage.  If we switch to 12v panels than Mptt might be necessary.

Also note that for max efficiency we should limit the charge current of the charger (via custom resistor) to match that as close to possible of the expected conditions in ther field or based on expected max output of panel..... so size charging rate to panel size.   It's documented on the adafruit page in great detail.    https://learn.adafruit.com/usb-dc-and-solar-lipoly-charger/using-the-charger

_____________________________________
Ed Verhamme
Project Engineer
501 Avis Drive, Ann Arbor, MI 48108
Office: 734-332-1200<tel:734-332-1200> Direct/Cell: 734-681-0577<tel:734-681-0577>
Email: everhamme@limno.com<mailto:everhamme@limno.com>
http://twitter.com/eddiegreatlakes
LimnoTech           www.limno.com<http://www.limno.com/>
Water Environment | Scientists Engineers

neilh10, 2019-03-07:
Great idea to move to 1A - that could mean a 8Ahr battery could be recharged in a solar day.

For an easy option to move to a higher voltage a 3pin plug-in switcher could be used. I have been thinking about could it built into the cable.  Its 3-pins are centered on 0.1" - so a fairly small footprint. It would require a different polarized 2pin connector for the higher solar voltage.   
(For the higher W solar panels an 18V typical can get to 30V on a cold day and no charge being taken) 
OKI-78SR-5/1.5-W36-C Vin=36V, Vout 5V@1.5A
https://www.digikey.com/products/en?keywords=811-2196-5-ND  $4.50

The MCP73871 is nice for its power-path switcher. That means that for a fully discharged LiIon (dead low voltage disconnect to processor) with weak sunshine (high impedance solar) - it will provide power to the uP before it starts charging the LiIon  - the uP needs to know that it can't place a heavy demand on the battery. There would be a benefit for a direct reliable LiIon battery V instead of the current USB V. ( I'm already testing this code for myself).

The current Mayfly MCP charger trickle charge a fully discharged battery till the LiIon voltage rises enough before allowing the full charge current. That of course can be annoying to a person sitting in front of the system trying to determine if its healthy as it won't come up for some time. 

There are some LiIon chargers that enable the charge current to be programmed by toggling the enable line - but I forget which ones now.

aufdenkampe, 2019-03-07:
@everhamme and @neilh10, thanks for your encouragement and input! (also, @everhamme gets credit for pointing me to the blog post from Voltaic!).

I really like the idea of keeping future versions of the Mayfly to be flexible, for a broad range of power needs. I also like the idea of sticking within the range of [Voltaic's small 6V solar panels](https://www.voltaicsystems.com/shop-gear/categories/solar-panels), which include 1, 2, 3.5, 6, and 9 W sizes. And I like the idea of sticking with the same JST connector that is broadly used in the DIY electronics world.

So maybe the upgrade is to the MCP73871 controller, but with the ability to switch between 0.5A or 1.0A charging, using something like the 3-pin switching jumpers near the Mayfly's grove ports?

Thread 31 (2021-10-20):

EnviroDIY/EnviroDIY_Mayfly_Logger #31: Xbee Decoupling capacitor

neilh10, 2021-10-20:
Cellular modules recommend a low ESR ceramic decoupling capacitor close to the power pins, with the lowest impedance current loop path. 
For Maylfly 1.0A3 there doesn't appear to be a large decoupling capcitor between BEE_VCC and GND, though perhaps the path through the regulator to the regulator's 10uF and low impedance LiIon battery wroks
Can a largish ceramic capacitor (100uf) be applied to Xbee pins. 
I'll post references to data sheets, but I have limited access this afternoon.

s-hicks2, 2021-11-03:
Sufficient power filtering capacitors are included on the EnviroDIY LTE sim7080 cell module, so no additional caps were added to the Mayfly 1.0.  But since some users might want to use the Digi brand LTE boards directly on the Mayfly, filtering cap(s) will be added to future versions.  Short term tests of the Digi LTE bee directly plugged into the Mayfly with no LTEbee adapter (making appropriate changes to the solder jumpers on the back of the Mayfly 1.0) showed no problems with battery power input.

aufdenkampe, 2021-11-03:
@s-hicks2, thanks for creating a new cellular modem for the EnviroDIY community. 

I agree with @neilh10 that the Mayfly v1 needs to support the Digi Xbee3 LTE-M modems -- both the older ones that we are already using and also the major revision that they are currently developing -- in addition to other future modems. Therefore, I think it is important to add that capacitor chain that @neilh10 displayed above.

neilh10, 2022-03-30:
The Mayfly 1.1 Xbee socket has a good capacitor decoupling for supporting an Digi Xbee LTE. Many thanks

closed 2022-03-30 by neilh10

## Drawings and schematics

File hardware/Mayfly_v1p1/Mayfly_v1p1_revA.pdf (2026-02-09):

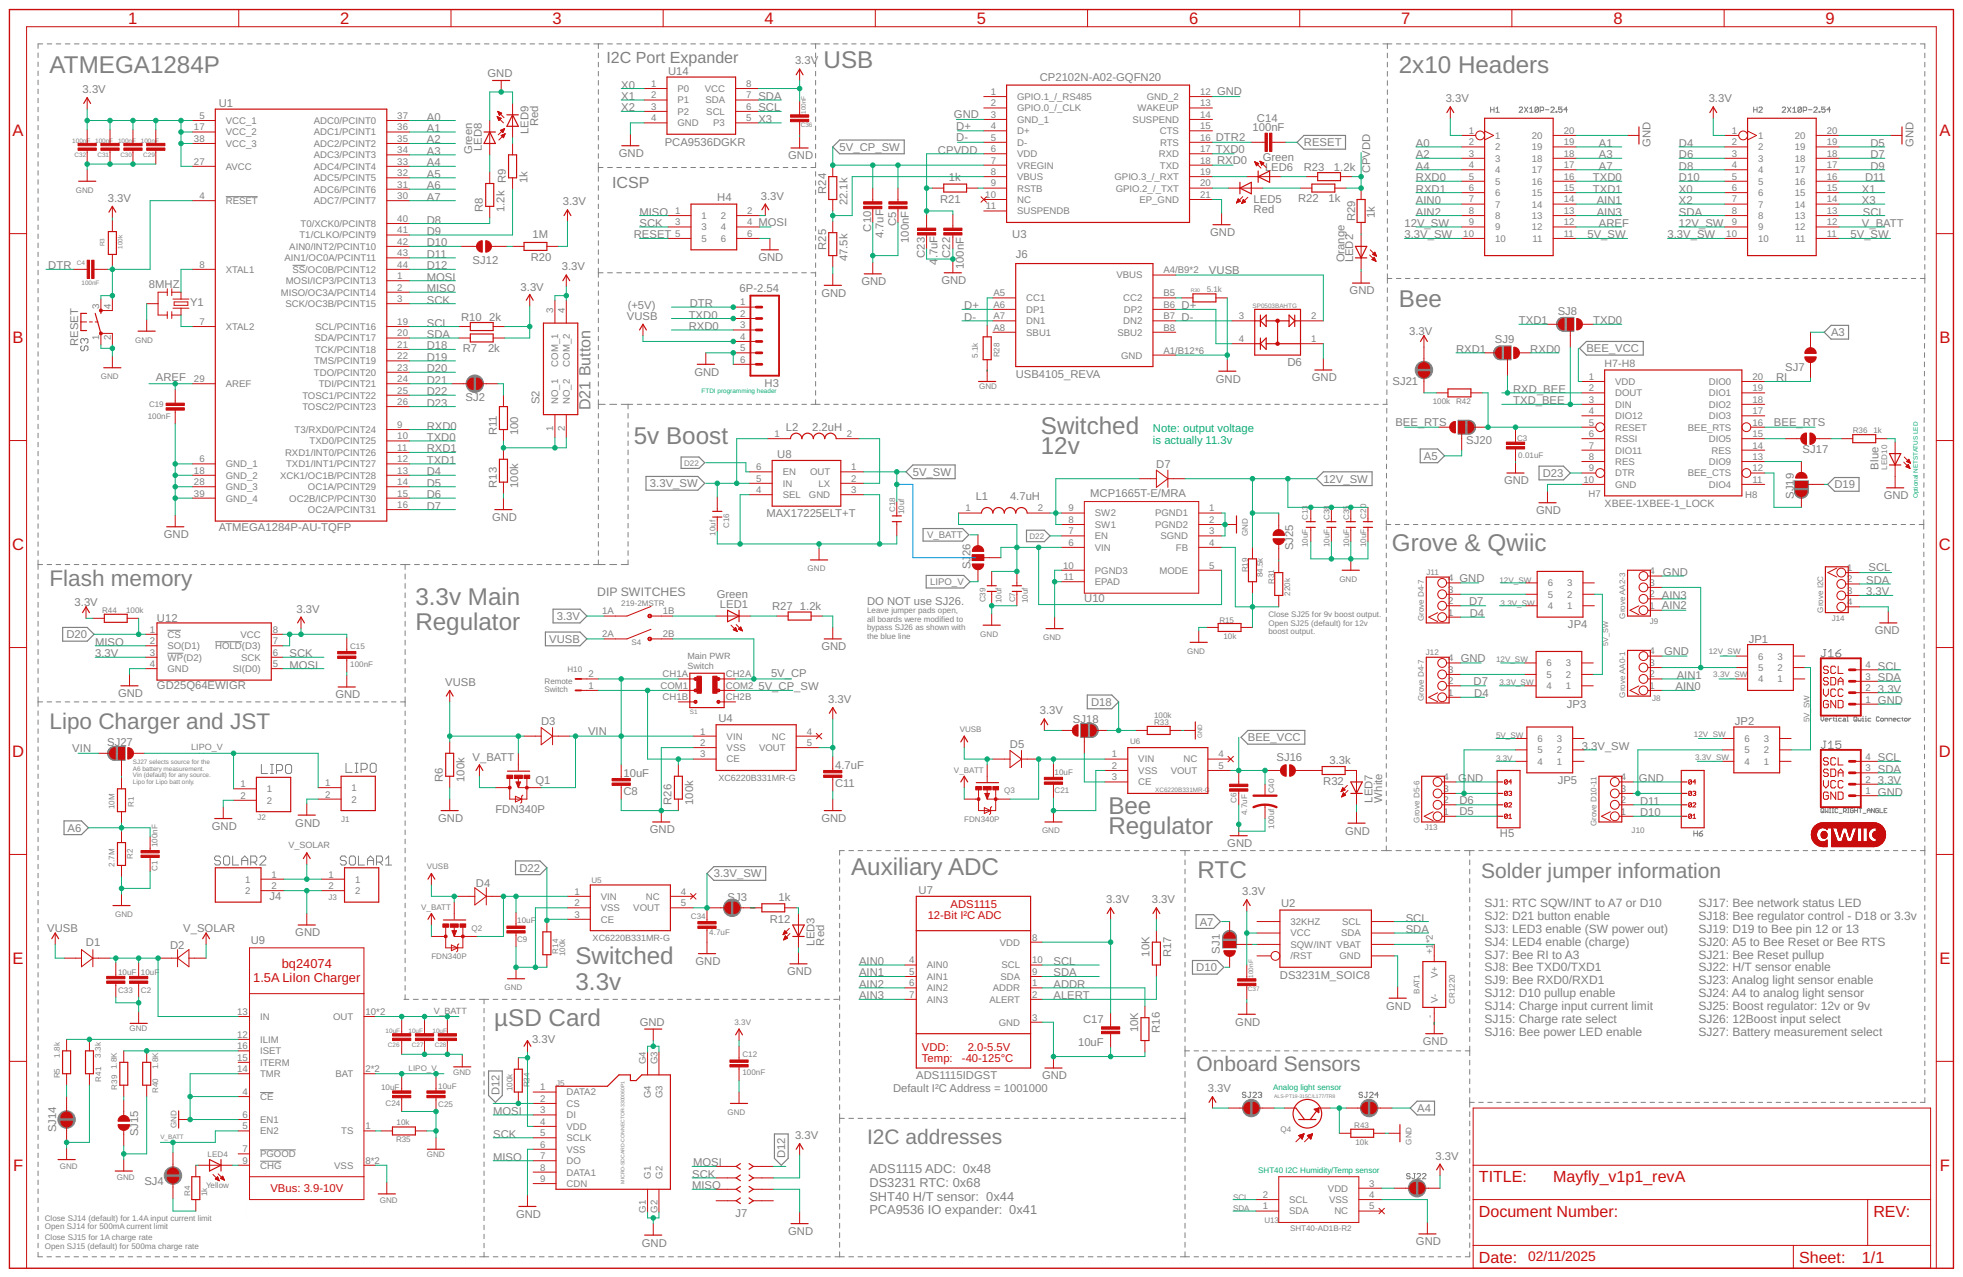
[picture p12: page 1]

DO NOT use SJ26. Leave jumper pads open, all boards were modified to

Close SJ25 for 9v boost output. Open SJ25 (default) for 12v boost output.

bypass SJ26 as shown with
the blue line

Lipo Charger and JST

SJ27 selects source for the A6 battery measurement. Vin (default) for any source. Lipo for Lipo batt only.

SJ1: RTC SQW/INT to A7 or D10
SJ2: D21 button enable SJ3: LED3 enable (SW power out)

SJ17: Bee network status LED
SJ18: Bee regulator control - D18 or 3.3v SJ19: D19 to Bee pin 12 or 13

SJ4: LED4 enable (charge)
SJ7: Bee RI to A3
SJ8: Bee TXD0/TXD1
SJ9: Bee RXD0/RXD1
SJ12: D10 pullup enable SJ14: Charge input current limit

SJ20: A5 to Bee Reset or Bee RTS
SJ21: Bee Reset pullup
SJ22: H/T sensor enable SJ23: Analog light sensor enable SJ24: A4 to analog light sensor SJ25: Boost regulator: 12v or 9v SJ26: 12Boost input select

MICRO-SDCARD-CONNECTOR-3300060P1 GND

SJ15: Charge rate select
SJ16: Bee power LED enable

Close SJ14 (default) for 1.4A input current limit Open SJ14 for 500mA current limit Close SJ15 for 1A charge rate Open SJ15 (default) for 500ma charge rate

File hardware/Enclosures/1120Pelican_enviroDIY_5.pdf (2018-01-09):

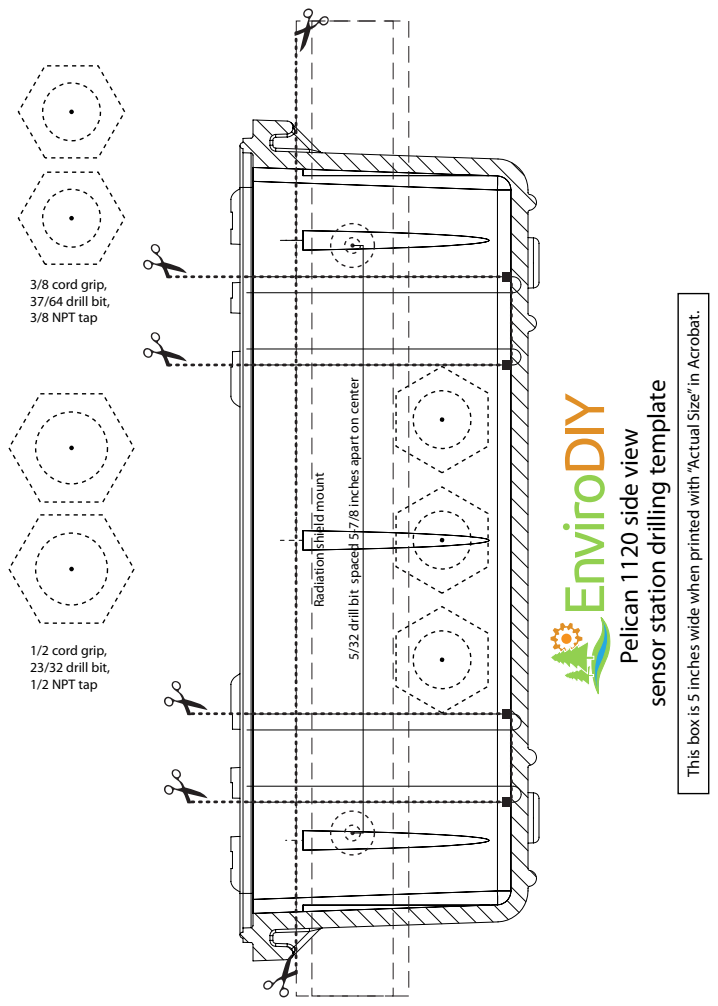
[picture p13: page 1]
3/8 cord grip, 37/64 drill bit, 3/8 NPT tap; 1/2 cord grip, 23/32 drill bit, 1/2 NPT tap; EnviroDIY

This box is 5 inches wide when printed with “Actual Size” in Acrobat.

5/32 drill bit spaced 5-7/8 inches apart on center

sensor station drilling template

Pelican 1120 side view

Radiation shield mount

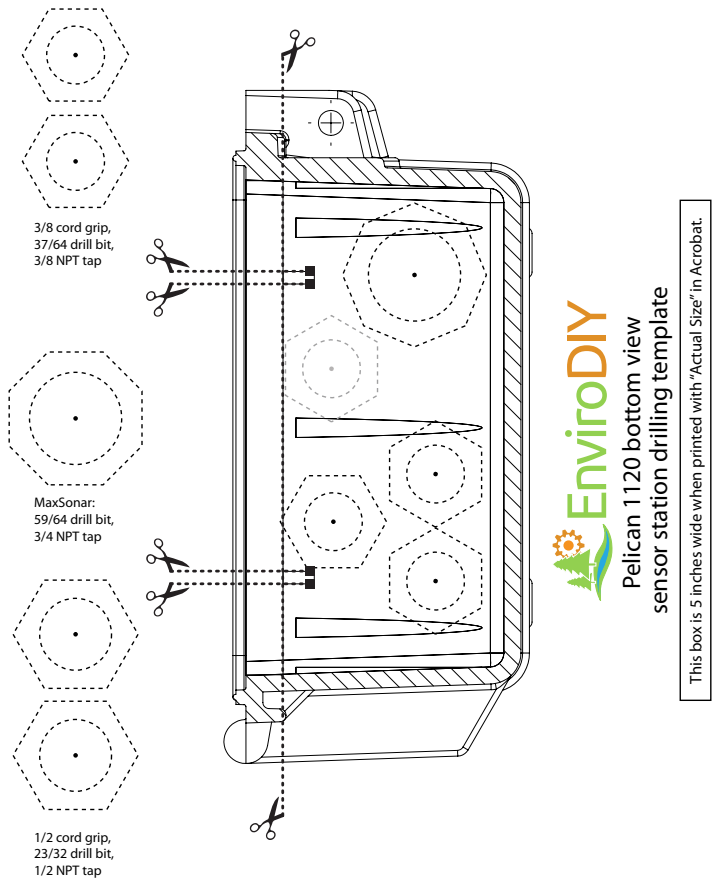
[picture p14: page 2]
3/8 cord grip, 37/64 drill bit, 3/8 NPT tap; 1/2 cord grip, 23/32 drill bit, 1/2 NPT tap; MaxSonar: 59/64 drill bit, 3/4 NPT tap; EnviroDIY

This box is 5 inches wide when printed with “Actual Size” in Acrobat.

sensor station drilling template

Pelican 1120 bottom view

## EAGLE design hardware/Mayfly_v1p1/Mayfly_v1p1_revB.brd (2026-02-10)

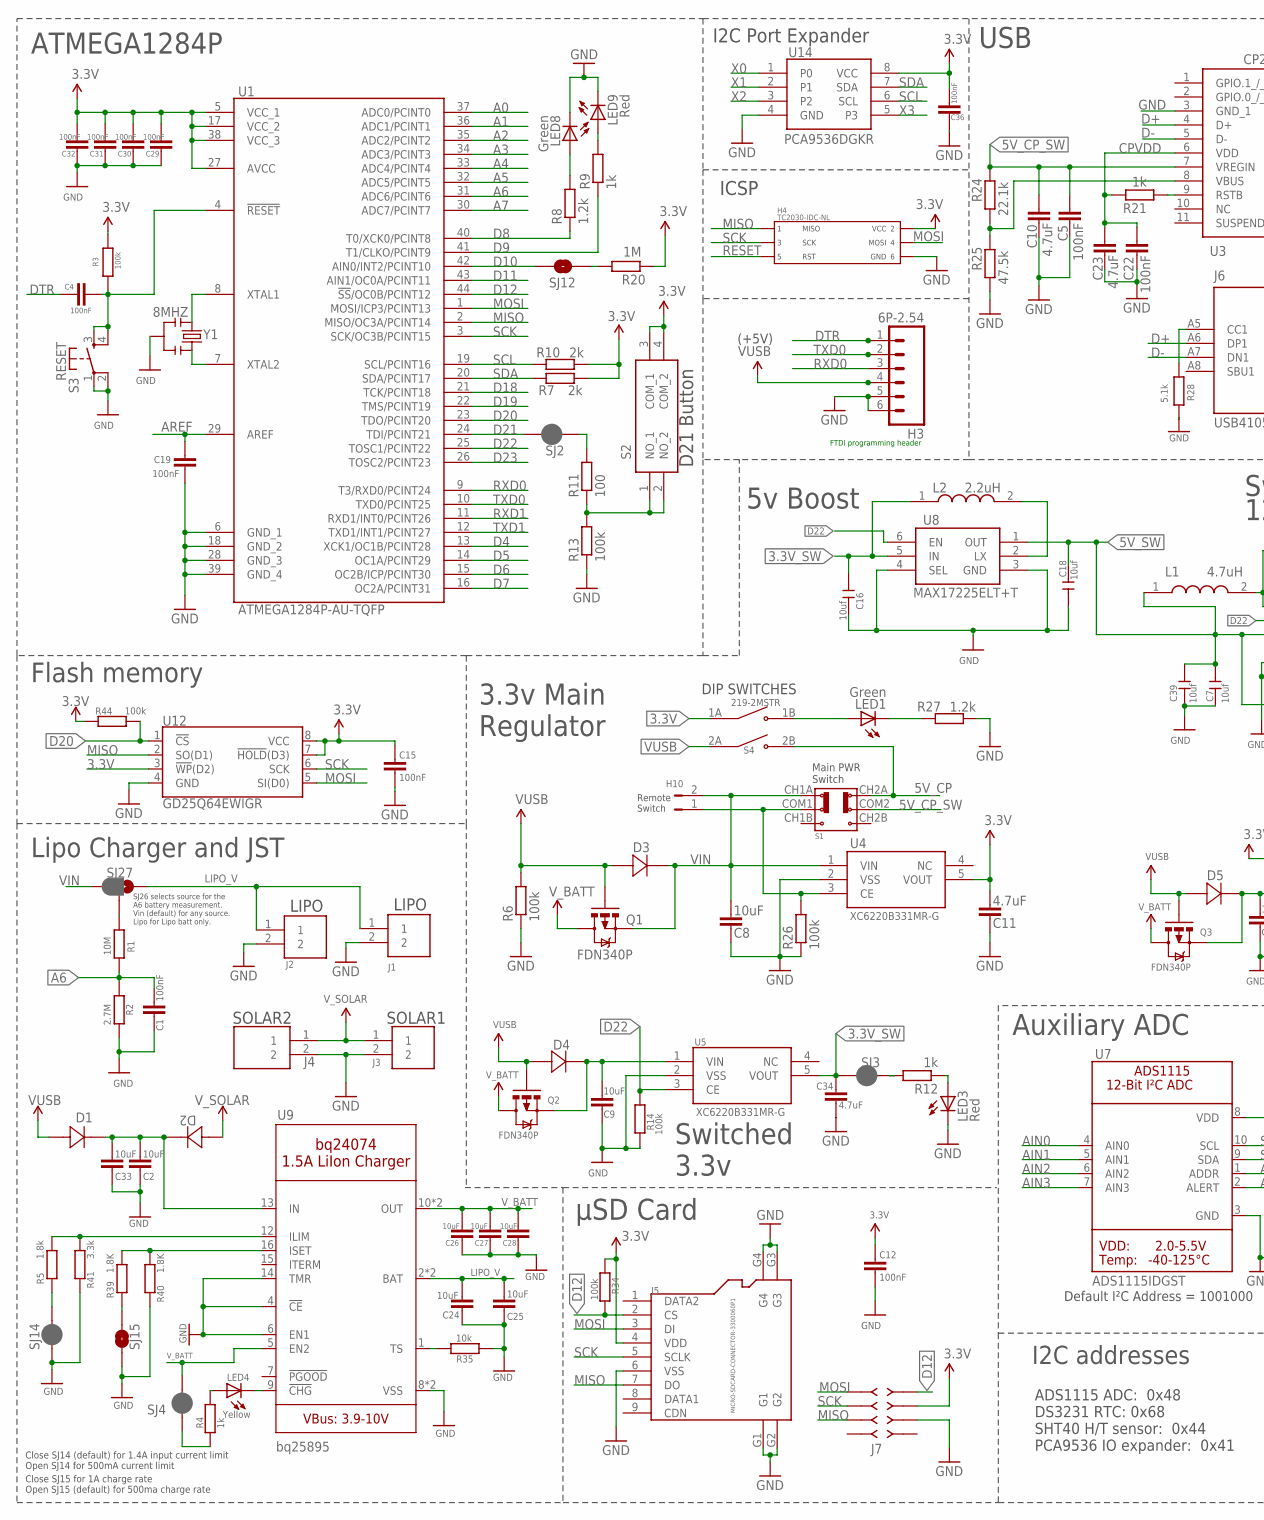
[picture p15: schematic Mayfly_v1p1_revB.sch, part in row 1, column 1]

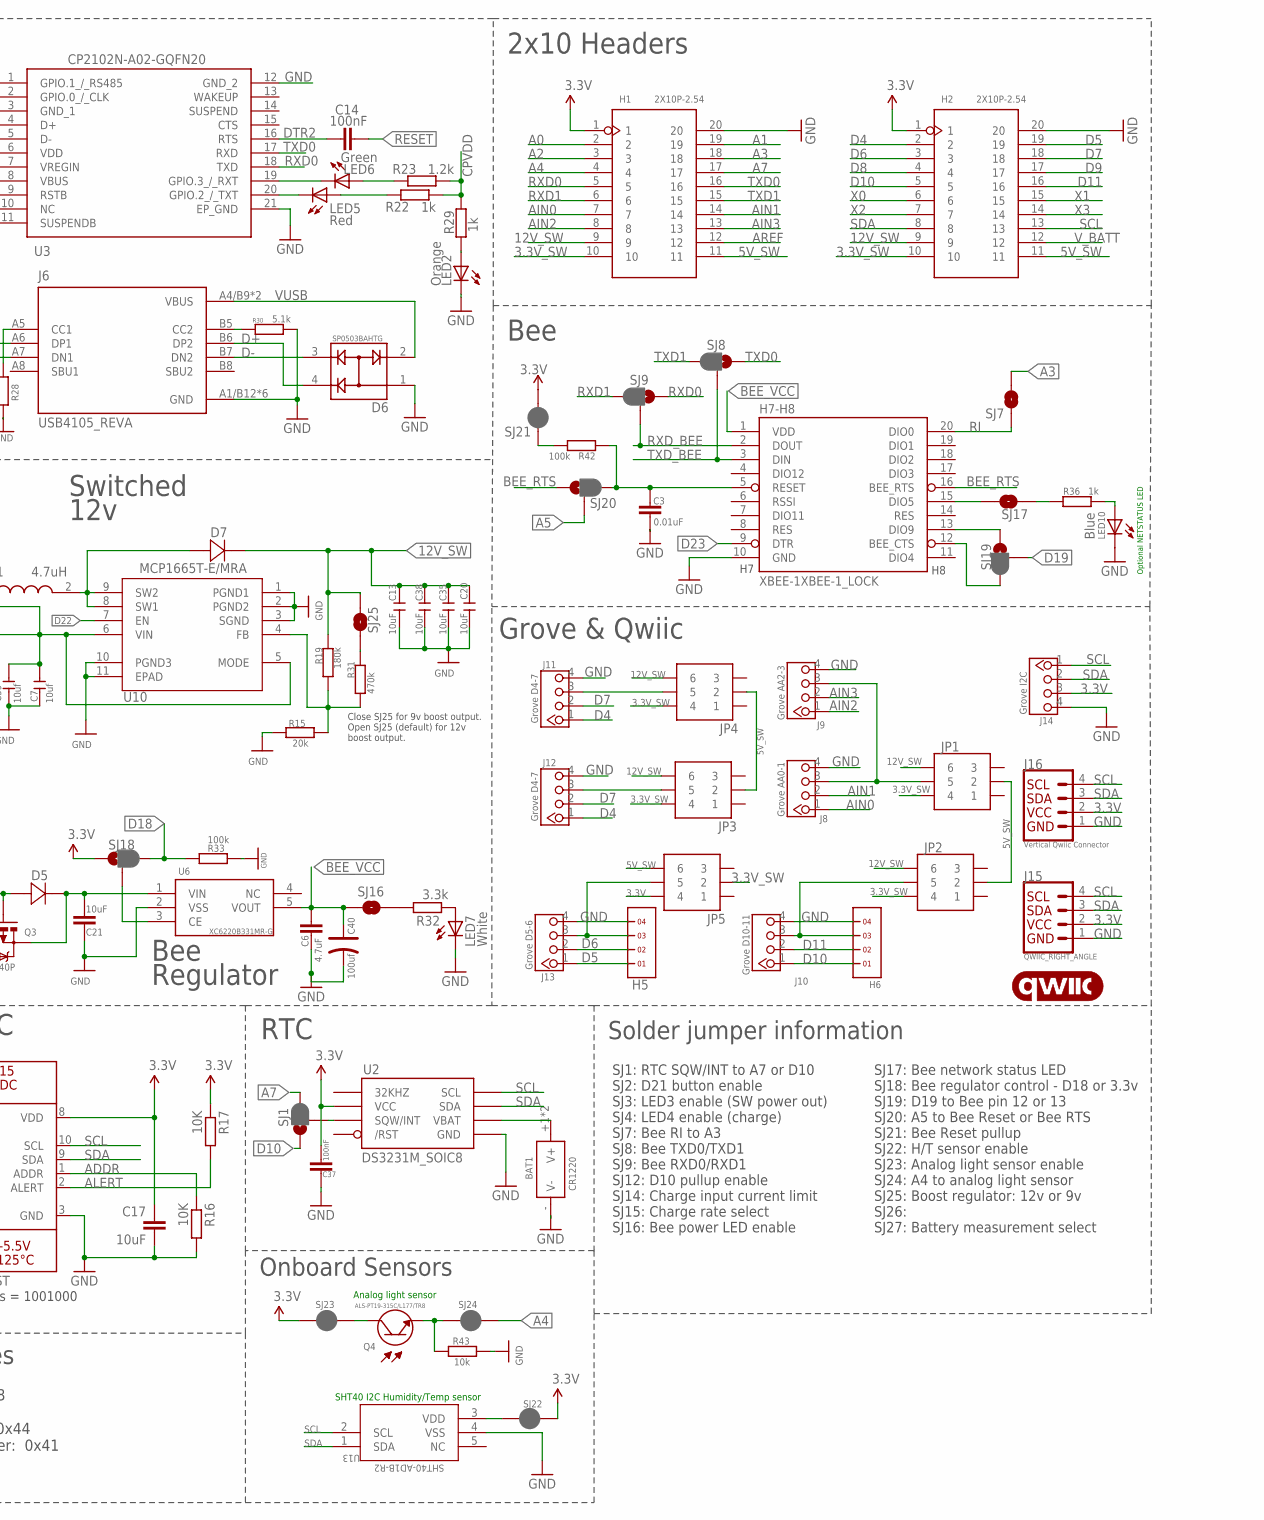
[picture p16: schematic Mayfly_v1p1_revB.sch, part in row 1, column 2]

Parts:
BAT1: CR1220; BAT2P-13.5-CR1220
C1, C4, C5, C12, C14, C22, C29, C30, C31, C32, C36, C37: 100nF; C0603
C2, C8, C9, C17, C21, C24, C25, C26, C27, C28, C33: 10uF; C0603
C3: 0.01uF; C0603
C6, C10, C11, C23, C34: 4.7uF; C0603
C7, C39: 10uf; C0805
C13, C20, C35, C38: 10uF; C1206
C15, C19: 100nF; C0402
C16, C18: 10uf; C0603
C40: 100uf; AVX-B
D1, D2, D3, D4, D5, D7: MSS2P2-M3/89A; DIODE_MSP3V3
D6: SP0503BAHTG; SOT143
H1, H2: 2X10P-2.54; H2X10-2.54
H3: 6P-2.54; 1X06_FEMALE_LOCK.010
H4: TC2030-IDC-NL
H5, H6: 1X4
H7-H8: XBEE-1XBEE-1_LOCK; XBEE-1_LOCK
H10: JUMPER-PTH-2-NO; PTH-JUMPER-2-NO_NO_SILK
J1, J2, J3: JST_EPH_2PIN; JST_EPH_B2B-PH-K-S
J4: 1778557; SHDR2W70P0X250_1X2_670X500X765
J5: MICRO-SDCARD-CONNECTOR-3300060P1; 9P-SMD-W-RING
J6: USB4105_REVA; GCT_USB4105_REVA
J7: 79107-08_S; 79107-08
J8: Grove AA0-1; HW4-2.0
J9: Grove AA2-3; HW4-2.0
J10: Grove D10-11; HW4-2.0
J11, J12: Grove D4-7; HW4-2.0
J13: Grove D5-6; HW4-2.0
J14: Grove I2C; HW4-2.0
J15: QWIIC_RIGHT_ANGLE; JST04_1MM_RA
J16: Vertical Qwiic Connector; JST04_1MM_VERT
JP1, JP2, JP3, JP4, JP5: M22-2520305; HDRV6W50P200_2X3_600X400X525P
L1: 4.7uH; XAL4030472MEC
L2: 2.2uH; 1285ASH1R0MP2
LED1, LED6, LED8: Green; LED-0603
LED2: Orange; LED-0603
LED3, LED5, LED9: Red; LED-0603
LED4: Yellow; LED-0603
LED7: White; LED-0603
LED10: Blue; LED-0603
LOGO4: QWIIC_LOGO_5MM; QWIIC_5MM
Q1, Q2, Q3: FDN340P; SOT23-S-PADS
Q4: ALS-PT19-315C/L177/TR8; XDCR_ALS-PT19-315C/L177/TR8
R1: 10M; R0402
R2: 2.7M; R0402
R3, R26: 100k; R0603
R4, R9, R12, R21, R22, R29, R36: 1k; R0402
R5: 1.8k; R0402
R6, R13, R14, R33, R34, R42, R44: 100k; R0402
R7, R10: 2k; R0603
R8, R23, R27: 1.2k; R0402
R11: 100; R0402
R15: 20k; R0402
R16, R17: 10K; R0402
R19: 180k; R0402
R20: 1M; R0603
R24: 22.1k; R0402
R25: 47.5k; R0402
R28, R30: 5.1k; R0402
R31: 470k; R0402
R32, R41: 3.3k; R0402
R35, R43: 10k; R0402
R39, R40: 1.8K; R0402
S1: SWITCH-2CH-6P-3010010P1; 6P-2CH-2.54-9.1X3.5X3.2+2H
S2: PTS647SK38SMTR2LFS
S3: MOMENTARY-SWITCH-SPST-2-SMD-4.6X2.8MM; TACTILE_SWITCH_SMD_4.6X2.8MM
S4: 219-2MSTR; SW_219-2MSTR
SJ1, SJ8, SJ9, SJ18, SJ19, SJ20, SJ27: JUMPER-SMT_3_1-NC_PASTE_SILK; SMT-JUMPER_3_1-NC_PASTE_SILK
SJ2, SJ3, SJ4, SJ14, SJ21, SJ22, SJ23, SJ24: JUMPER-SMT_2_NC_PASTE_SILK; SMT-JUMPER_2_NC_PASTE_SILK
SJ7, SJ15, SJ16, SJ17, SJ25: JUMPER-SMT_2_NO_SILK; SMT-JUMPER_2_NO_SILK
SJ12: SOLDERJUMPERNO; SJ_2S-NO
U1: ATMEGA1284P-AU-TQFP; QFP80P1200X1200X120-44N
U2: DS3231M_SOIC8; SO8
U3: CP2102N-A02-GQFN20; CP2102NA02GQFN20
U4, U5, U6: XC6220B331MR-G; SOT95P280X130-5N
U7: ADS1115IDGST; MSOP10
U8: MAX17225ELT+T; MAX17225ELTT
U9: ADAFRUIT_POWER_BQ24074; ADAFRUIT_POWER_QFN16_3MM
U10: MCP1665T-E/MRA; QFN50P200X200X90-11N
U12: GD25Q64EWIGR; WSON8-6X5MM
U13: SHT40-AD1B-R2; SHT4X_SEN
U14: PCA9536DGKR; SOP65P490X110-8N
Y1: 8MHZ; X3-SMD-3.6X1.3X0.8MM

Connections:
3.3V: C11.2, C12.2, C15.2, C17.1, C29.2, C30.2, C31.2, C32.2, C36.2, C37.2, H1.1, H2.1, H4.P$2 (PIN2), J5.4 (VDD), J7.3, J14.3, J15.2, J16.2, JP5.4, R3.2, R7.1, R10.2, R17.1, R20.2, R34.1, R44.1, S2.3 (COM_1), S2.4 (COM_2), S4.1A (COM1), SJ18.1, SJ21.2, SJ22.1, SJ23.1, U1.5 (VCC_1), U1.17 (VCC_2), U1.27 (AVCC), U1.38 (VCC_3), U2.2 (VCC), U4.5 (VOUT), U7.8 (VDD), U12.3 (!WP!(D2)), U12.7 (!HOLD!(D3)), U12.8 (VCC), U14.8 (VCC)
3.3V_SW: C16.2, C34.2, H1.10, H2.10, JP1.4, JP2.4, JP3.4, JP4.4, JP5.2, L2.1, SJ3.1, U5.5 (VOUT), U8.5 (IN)
5V_CP: S1.CH2A, S4.2B (NO2)
5V_CP_SW: C5.2, C10.2, R24.2, S1.COM2, U3.7 (VREGIN)
5V_SW: C7.1, C18.1, C39.1, H1.11, H2.11, JP1.2, JP2.2, JP3.2, JP4.2, JP5.6, L1.1, U8.1 (OUT), U10.5 (MODE), U10.6 (VIN)
12V_SW: C13.2, C20.2, C35.2, C38.2, D7.1, H1.9, H2.9, JP1.6, JP2.6, JP3.6, JP4.6, R19.1, SJ25.2
A0: H1.2, U1.37 (ADC0/PCINT0)
A1: H1.19, U1.36 (ADC1/PCINT1)
A2: H1.3, U1.35 (ADC2/PCINT2)
A3: H1.18, SJ7.2, U1.34 (ADC3/PCINT3)
A4: H1.4, SJ24.2, U1.33 (ADC4/PCINT4)
A5: SJ20.2, U1.32 (ADC5/PCINT5)
A6: C1.2, R1.1, R2.2, U1.31 (ADC6/PCINT6)
A7: H1.17, SJ1.3, U1.30 (ADC7/PCINT7)
ADDR: R16.1, U7.1 (ADDR)
AIN0: H1.7, J8.1, U7.4 (AIN0)
AIN1: H1.14, J8.2, U7.5 (AIN1)
AIN2: H1.8, J9.1, U7.6 (AIN2)
AIN3: H1.13, J9.2, U7.7 (AIN3)
ALERT: R17.2, U7.2 (ALERT)
AREF: C19.2, H1.12, U1.29 (AREF)
BEE_RTS: H7-H8.16 (BEE_RTS), SJ20.1
BEE_VCC: C6.2, C40.+, H7-H8.1 (VDD), SJ16.1, U6.5 (VOUT)
BQ_IN: C2.2, C33.2, D1.1, D2.1, U9.13 (IN)
C: U1.8 (XTAL1), Y1.1
CPVDD: C22.2, C23.2, R21.2, R22.1, R23.1, R29.1, U3.6 (VDD)
C_N: U1.7 (XTAL2), Y1.3
D4: H2.2, J11.1, J12.1, U1.13 (XCK1/OC1B/PCINT28)
D5: H2.19, H5.1, J13.1, U1.14 (OC1A/PCINT29)
D6: H2.3, H5.2, J13.2, U1.15 (OC2B/ICP/PCINT30)
D7: H2.18, J11.2, J12.2, U1.16 (OC2A/PCINT31)
D8: H2.4, R8.1, U1.40 (T0/XCK0/PCINT8)
D9: H2.17, R9.1, U1.41 (T1/CLKO/PCINT9)
D10: H2.5, H6.1, J10.1, SJ1.1, SJ12.1, U1.42 (AIN0/INT2/PCINT10)
D11: H2.16, H6.2, J10.2, U1.43 (AIN1/OC0A/PCINT11)
D12: J5.2 (CS), J7.1, R34.2, U1.44 (!SS!/OC0B/PCINT12)
D18: R33.2, SJ18.3, U1.21 (TCK/PCINT18)
D19: SJ19.2, U1.22 (TMS/PCINT19)
D20: R44.2, U1.23 (TDO/PCINT20), U12.1 (!CS!)
D21: SJ2.2, U1.24 (TDI/PCINT21)
D22: R14.2, U1.25 (TOSC1/PCINT22), U5.3 (CE), U8.6 (EN), U10.7 (EN)
D23: H7-H8.9 (DTR), U1.26 (TOSC2/PCINT23)
D+: D6.4, J6.A6 (DP1), J6.B6 (DP2), U3.4 (D+)
D-: D6.3, J6.A7 (DN1), J6.B7 (DN2), U3.5 (D-)
DTR: C4.1, H3.1
DTR2: C14.2, U3.16 (RTS)
GND: BAT1.- (V-), C1.1, C2.1, C3.1, C5.1, C6.1, C7.2, C8.1, C9.1, C10.1, C11.1, C12.1, C13.1, C15.1, C16.1, C17.2, C18.2, C19.1, C20.1, C21.1, C22.1, C23.1, C24.1, C25.1, C26.1, C27.1, C28.1, C29.1, C30.1, C31.1, C32.1, C33.1, C34.1, C35.1, C36.1, C37.1, C38.1, C39.2, C40.-, D6.1, H1.20, H2.20, H3.5, H3.6, H4.P$6 (PIN6), H5.4, H6.4, H7-H8.10 (GND), J1.2, J2.2, J3.2, J4.2, J5.6 (VSS), J5.G1, J5.G2, J5.G3, J5.G4, J6.A1/B12 (GND), J6.B1/A12 (GND), J6.G1 (GND), J6.G2 (GND), J6.G3 (GND), J6.G4 (GND), J7.5, J8.4, J9.4, J10.4, J11.4, J12.4, J13.4, J14.4, J15.1, J16.1, LED2.C, LED3.C, LED7.C, LED8.C, LED9.C, LED10.C, R2.1, R6.1, R13.1, R14.1, R15.2, R16.2, R25.1, R26.1, R27.1, R28.2, R30.2, R33.1, R35.1, R40.1, R41.1, R43.2, S3.1, S3.2, SJ14.2, SJ15.1, U1.6 (GND_1), U1.18 (GND_2), U1.28 (GND_3), U1.39 (GND_4), U2.5 (GND), U3.3 (GND_1), U3.12 (GND_2), U3.21 (EP_GND), U4.2 (VSS), U5.2 (VSS), U6.2 (VSS), U7.3 (GND), U8.3 (GND), U8.4 (SEL), U9.4 (!CE), U9.6 (EN1), U9.8 (VSS), U9.14 (TMR), U9.THERMAL (VSS), U10.1 (PGND1), U10.2 (PGND2), U10.3 (SGND), U10.10 (PGND3), U10.11 (EPAD), U12.4 (GND), U13.4 (VSS)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
LIPO_V: C24.2, C25.2, J1.1, J2.1, SJ27.1, U9.2 (BAT), U9.3 (BAT)
MISO: H4.P$1 (PIN1), J5.7 (DO), J7.6, U1.2 (MISO/OC3A/PCINT14), U12.2 (SO(D1))
MOSI: H4.P$4 (PIN4), J5.3 (DI), J7.2, U1.1 (MOSI/ICP3/PCINT13), U12.5 (SI(D0))
unnamed: R20.1, SJ12.2
unnamed: H10.1, R26.2, S1.COM1, U4.3 (CE)
unnamed: R12.2, SJ3.2
unnamed: LED3.A, R12.1
unnamed: R11.1, R13.2, S2.1 (NO_1), S2.2 (NO_2)
unnamed: J8.3, J9.3, JP1.5
unnamed: R21.1, U3.9 (RSTB)
unnamed: R1.2, SJ27.2
unnamed: SJ18.2, U6.3 (CE)
unnamed: SJ1.2, U2.3 (SQW/INT)
unnamed: J6.A5 (CC1), R28.1
unnamed: LED4.A, R4.2
unnamed: R39.1, SJ15.2
unnamed: H7-H8.13 (DIO9), SJ19.1
unnamed: R4.1, SJ4.2
unnamed: D7.2, L1.2, U10.8 (SW1), U10.9 (SW2)
unnamed: R5.1, SJ14.1
unnamed: R11.2, SJ2.1
unnamed: J11.3, JP4.5
unnamed: LED1.C, R27.2
unnamed: H7-H8.12 (BEE_CTS), SJ19.3
unnamed: C3.2, H7-H8.5 (RESET), R42.1, SJ20.3
unnamed: C9.2, D4.1, Q2.2 (S), U5.1 (VIN)
unnamed: R15.1, R19.2, R31.2, U10.4 (FB)
unnamed: H6.3, J10.3, JP2.5
unnamed: LED1.A, S4.1B (NO1)
unnamed: H7-H8.15 (DIO5), SJ17.2
unnamed: J6.B5 (CC2), R30.1
unnamed: LED5.C, U3.20 (GPIO.2_/_TXT)
unnamed: LED6.C, U3.19 (GPIO.3_/_RXT)
unnamed: LED5.A, R22.2
unnamed: LED6.A, R23.2
unnamed: LED2.A, R29.2
unnamed: LED9.A, R9.2
unnamed: BAT1.+1 (V+), BAT1.+2 (V+), U2.6 (VBAT)
unnamed: LED8.A, R8.2
unnamed: LED7.A, R32.1
unnamed: R32.2, SJ16.2
unnamed: C21.2, D5.1, Q3.2 (S), U6.1 (VIN)
unnamed: LED10.A, R36.2
unnamed: R35.2, U9.1 (TS)
unnamed: LED4.C, U9.9 (!CHG)
unnamed: R42.2, SJ21.1
unnamed: R5.2, R41.2, U9.12 (ILIM)
unnamed: R39.2, R40.2, U9.16 (ISET)
unnamed: R36.1, SJ17.1
unnamed: SJ22.2, U13.3 (VDD)
unnamed: Q4.2 (E), R43.1, SJ24.1
unnamed: Q4.1 (C), SJ23.2
unnamed: H5.3, J13.3, JP5.5
unnamed: L2.2, U8.2 (LX)
unnamed: J12.3, JP3.5
unnamed: R31.1, SJ25.1
RESET: C4.2, C14.1, H4.P$5 (PIN5), R3.1, S3.3, S3.4, U1.4 (!RESET)
RI: H7-H8.20 (DIO0), SJ7.1
RXD0: H1.5, H3.3, SJ9.1, U1.9 (T3/RXD0/PCINT24), U3.18 (TXD)
RXD1: H1.6, SJ9.3, U1.11 (RXD1/INT0/PCINT26)
RXD_BEE: H7-H8.2 (DOUT), SJ9.2
SCK: H4.P$3 (PIN3), J5.5 (SCLK), J7.4, U1.3 (SCK/OC3B/PCINT15), U12.6 (SCK)
SCL: H2.13, J14.1, J15.4, J16.4, R10.1, U1.19 (SCL/PCINT16), U2.8 (SCL), U7.10 (SCL), U13.2 (SCL), U14.6 (SCL)
SDA: H2.8, J14.2, J15.3, J16.3, R7.2, U1.20 (SDA/PCINT17), U2.7 (SDA), U7.9 (SDA), U13.1 (SDA), U14.7 (SDA)
TXD0: H1.16, H3.2, SJ8.1, U1.10 (TXD0/PCINT25), U3.17 (RXD)
TXD1: H1.15, SJ8.3, U1.12 (TXD1/INT1/PCINT27)
TXD_BEE: H7-H8.3 (DIN), SJ8.2
VBS: R24.1, R25.2, U3.8 (VBUS)
VIN: C8.2, D3.1, H10.2, Q1.2 (S), S1.CH1A, SJ27.3, U4.1 (VIN)
VUSB: D1.2, D3.2, D4.2, D5.2, D6.2, H3.4, J6.A4/B9 (VBUS), J6.B4/A9 (VBUS), Q1.1 (G), Q2.1 (G), Q3.1 (G), R6.2, S4.2A (COM2)
V_BATT: C26.2, C27.2, C28.2, H2.12, Q1.3 (D), Q2.3 (D), Q3.3 (D), SJ4.1, U9.5 (EN2), U9.10 (OUT), U9.11 (OUT)
V_SOLAR: D2.2, J3.1, J4.1
X0: H2.6, U14.1 (P0)
X1: H2.15, U14.2 (P1)
X2: H2.7, U14.3 (P2)
X3: H2.14, U14.5 (P3)

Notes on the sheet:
ATMEGA1284P
Bee
Lipo Charger and JST
RTC
SOLAR1
LIPO
3.3v Main Regulator
(+5V)
USB
µSD Card
ICSP
Auxiliary ADC
Default I²C Address = 1001000
2x10 Headers
D21 Button
Close SJ14 (default) for 1.4A input current limit Open SJ14 for 500mA current limit
Close SJ15 for 1A charge rate Open SJ15 (default) for 500ma charge rate
SOLAR2
SHT40 I2C Humidity/Temp sensor
Analog light sensor
Switched 3.3v
Bee Regulator
Onboard Sensors
DIP SWITCHES
Remote Switch
Main PWR Switch
Optional NETSTATUS LED
Grove & Qwiic
FTDI programming header
I2C Port Expander
Switched 12v
5v Boost
Flash memory
Solder jumper information
SJ1: RTC SQW/INT to A7 or D10 SJ2: D21 button enable SJ3: LED3 enable (SW power out) SJ4: LED4 enable (charge) SJ7: Bee RI to A3 SJ8: Bee TXD0/TXD1 SJ9: Bee RXD0/RXD1 SJ12: D10 pullup enable SJ14: Charge input current limit SJ15: Charge rate select SJ16: Bee power LED enable
SJ17: Bee network status LED SJ18: Bee regulator control - D18 or 3.3v SJ19: D19 to Bee pin 12 or 13 SJ20: A5 to Bee Reset or Bee RTS SJ21: Bee Reset pullup SJ22: H/T sensor enable SJ23: Analog light sensor enable SJ24: A4 to analog light sensor SJ25: Boost regulator: 12v or 9v SJ26: SJ27: Battery 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
I2C addresses
ADS1115 ADC: 0x48 DS3231 RTC: 0x68 SHT40 H/T sensor: 0x44 PCA9536 IO expander: 0x41
Close SJ25 for 9v boost output. Open SJ25 (default) for 12v boost output.
SJ26 selects source for the A6 battery measurement. Vin (default) for any source. Lipo for Lipo batt only.

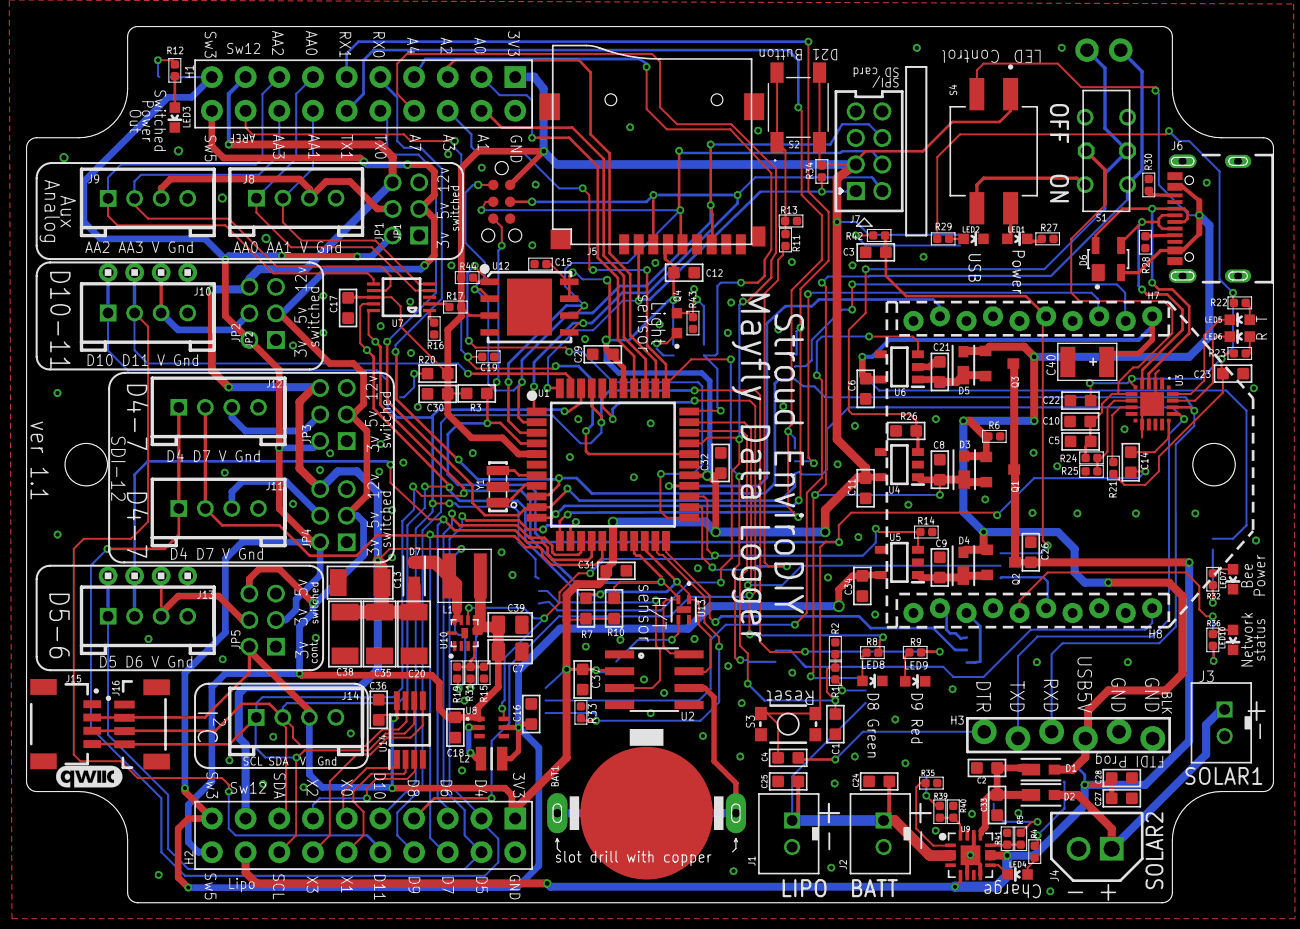
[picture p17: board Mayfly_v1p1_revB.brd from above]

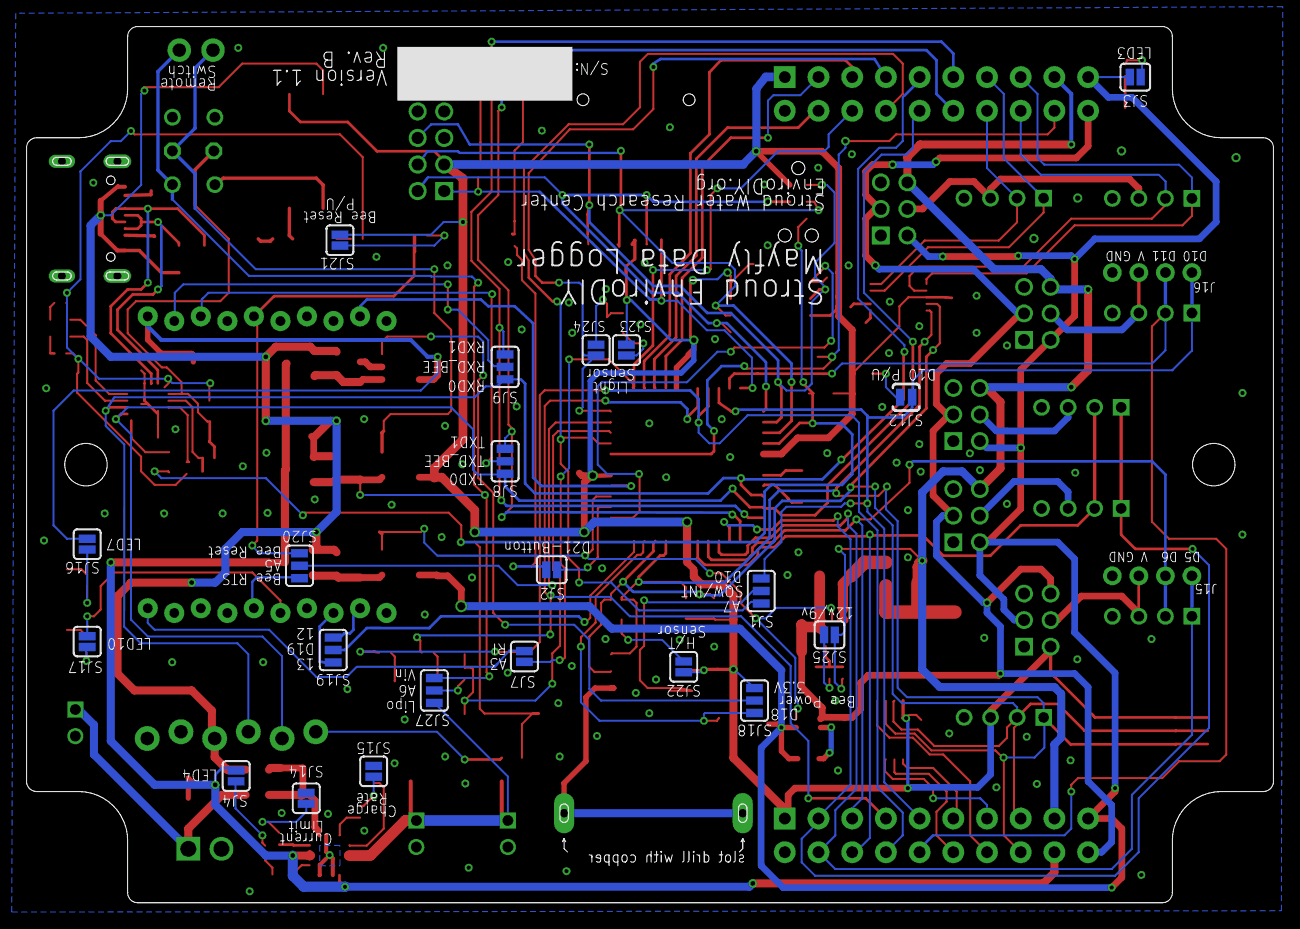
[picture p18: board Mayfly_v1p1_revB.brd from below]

Board: 4 copper layers, 94.0 x 66.0 mm, 174 parts (21 on the bottom side), 123 nets.

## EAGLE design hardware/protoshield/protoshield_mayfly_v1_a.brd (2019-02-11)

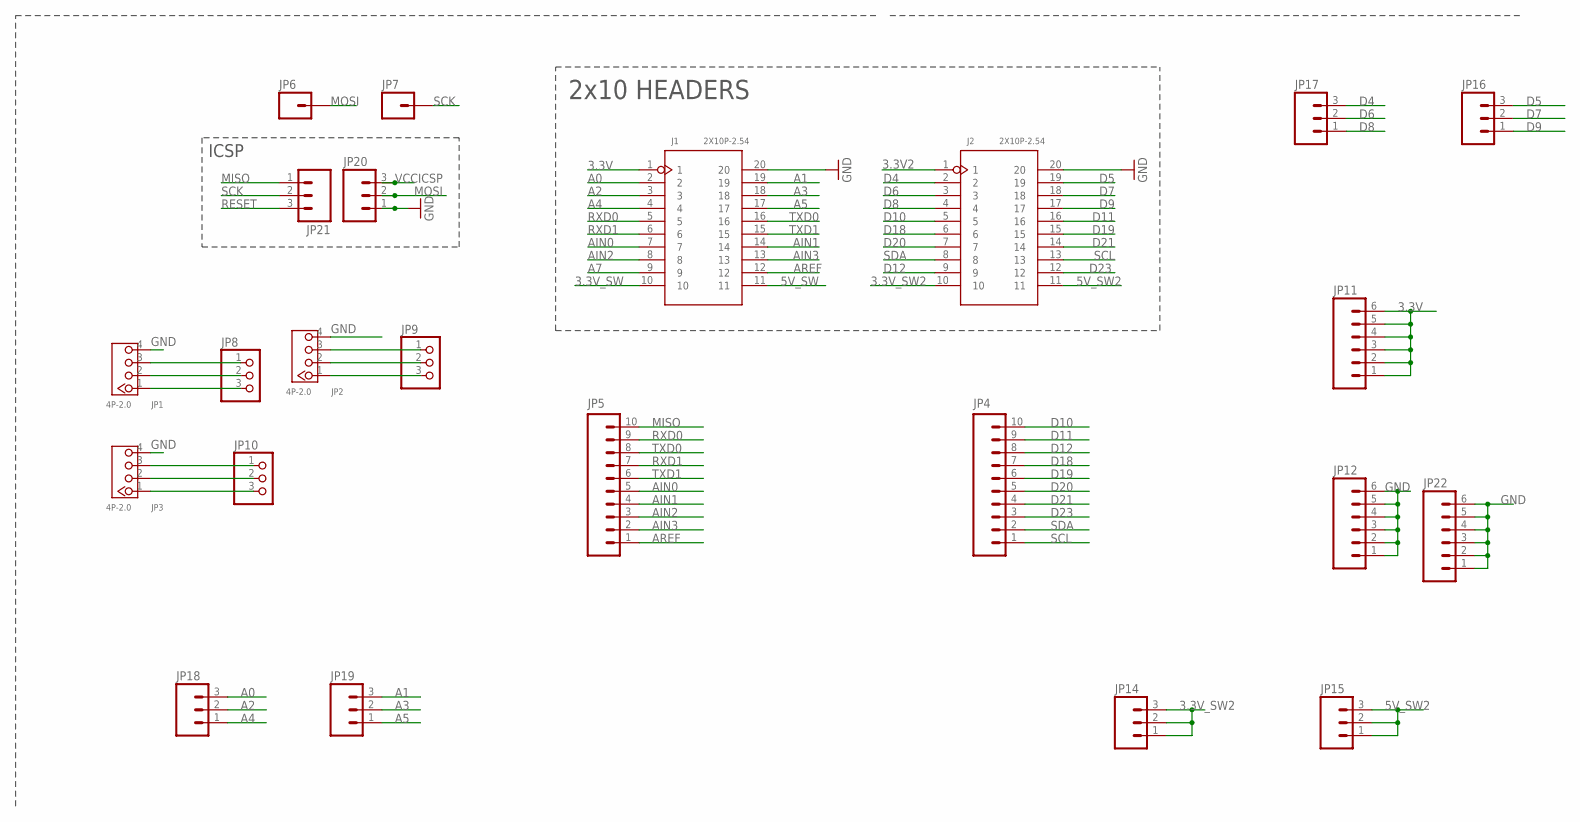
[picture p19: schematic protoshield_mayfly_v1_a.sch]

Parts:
J1, J2: 2X10P-2.54; H2X10-2.54
JP1, JP2, JP3: 4P-2.0; HW4-2.0
JP4, JP5: M10NO_SILK_PTH_FEMALE; 1X10_NO_SILK
JP6, JP7: M01PTH_NO_SILK_YES_STOP; 1X01_NO_SILK
JP8, JP9, JP10: PINHD-1X3CB; 1X03-CLEANBIG
JP11: M06NO_SILK_FEMALE_PTH; 1X06_NO_SILK
JP12, JP22: M06NO_SILK_YES_STOP; 1X06_NO_SILK_YES_STOP
JP14, JP15, JP16, JP17, JP18, JP19, JP20, JP21: M031X03_NO_SILK; 1X03_NO_SILK

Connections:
3.3V: J1.1, JP11.1, JP11.2, JP11.3, JP11.4, JP11.5, JP11.6
3.3V2: J2.1
3.3V_SW: J1.10
3.3V_SW2: J2.10, JP14.1, JP14.2, JP14.3
5V_SW: J1.11
5V_SW2: J2.11, JP15.1, JP15.2, JP15.3
A0: J1.2, JP18.3
A1: J1.19, JP19.3
A2: J1.3, JP18.2
A3: J1.18, JP19.2
A4: J1.4, JP18.1
A5: J1.17, JP19.1
A7: J1.9
AIN0: J1.7, JP5.5
AIN1: J1.14, JP5.4
AIN2: J1.8, JP5.3
AIN3: J1.13, JP5.2
AREF: J1.12, JP5.1
D4: J2.2, JP17.3
D5: J2.19, JP16.3
D6: J2.3, JP17.2
D7: J2.18, JP16.2
D8: J2.4, JP17.1
D9: J2.17, JP16.1
D10: J2.5, JP4.10
D11: J2.16, JP4.9
D12: J2.9, JP4.8
D18: J2.6, JP4.7
D19: J2.15, JP4.6
D20: J2.7, JP4.5
D21: J2.14, JP4.4
D23: J2.12, JP4.3
GND: J1.20, J2.20, JP1.4, JP2.4, JP3.4, JP12.1, JP12.2, JP12.3, JP12.4, JP12.5, JP12.6, JP20.1, JP22.1, JP22.2, JP22.3, JP22.4, JP22.5, JP22.6
MISO: JP5.10, JP21.1
MOSI: JP6.1, JP20.2
unnamed: JP1.1, JP8.3
unnamed: JP1.2, JP8.2
unnamed: JP1.3, JP8.1
unnamed: JP3.1, JP10.3
unnamed: JP3.2, JP10.2
unnamed: JP3.3, JP10.1
unnamed: JP2.3, JP9.1
unnamed: JP2.1, JP9.3
unnamed: JP2.2, JP9.2
RESET: JP21.3
RXD0: J1.5, JP5.9
RXD1: J1.6, JP5.7
SCK: JP7.1, JP21.2
SCL: J2.13, JP4.1
SDA: J2.8, JP4.2
TXD0: J1.16, JP5.8
TXD1: J1.15, JP5.6
VCCICSP: JP20.3

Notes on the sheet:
ICSP
2x10 HEADERS

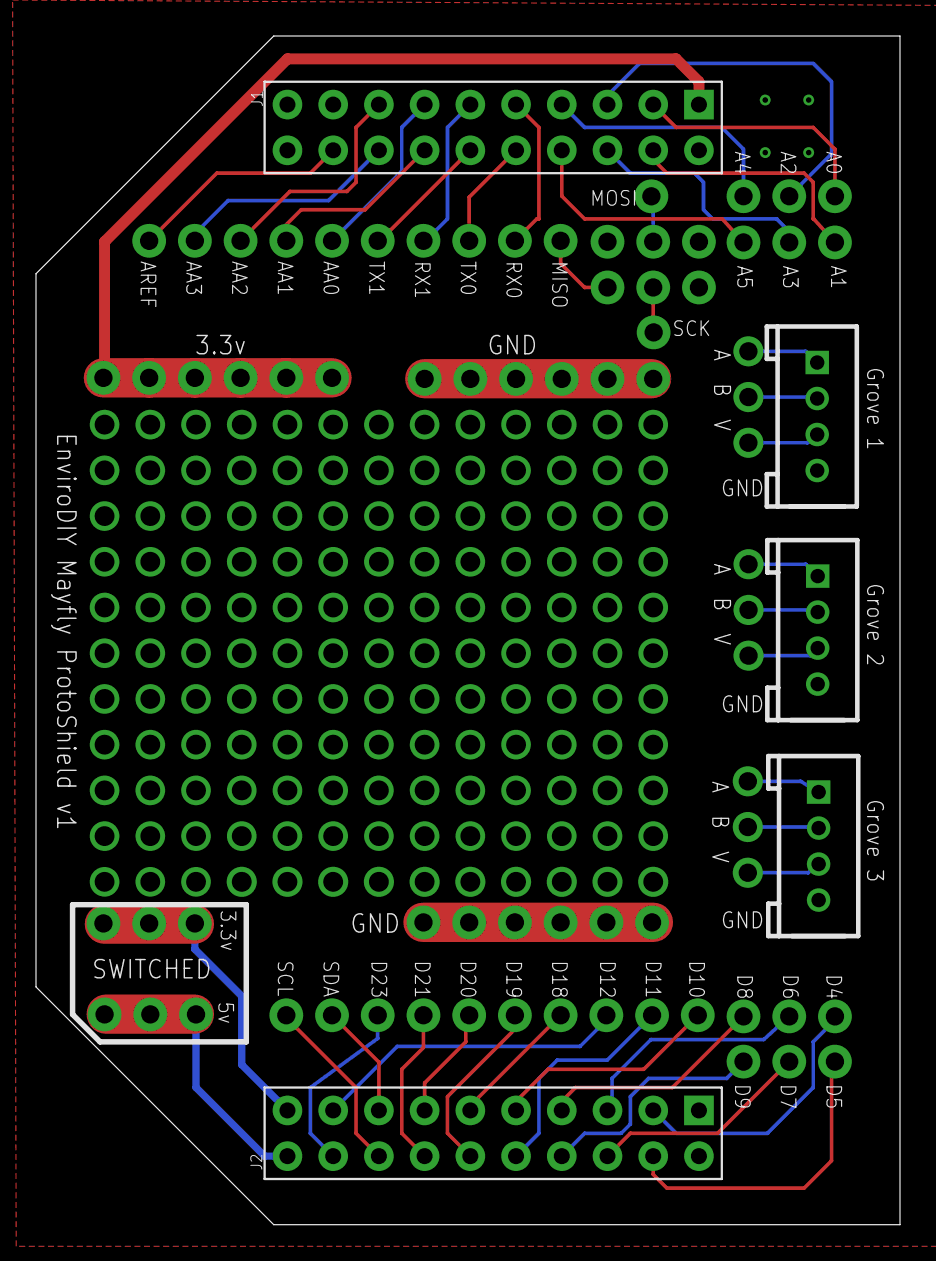
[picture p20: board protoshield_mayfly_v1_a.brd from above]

Board: 2 copper layers, 48.0 x 66.0 mm, 23 parts (0 on the bottom side), 47 nets.

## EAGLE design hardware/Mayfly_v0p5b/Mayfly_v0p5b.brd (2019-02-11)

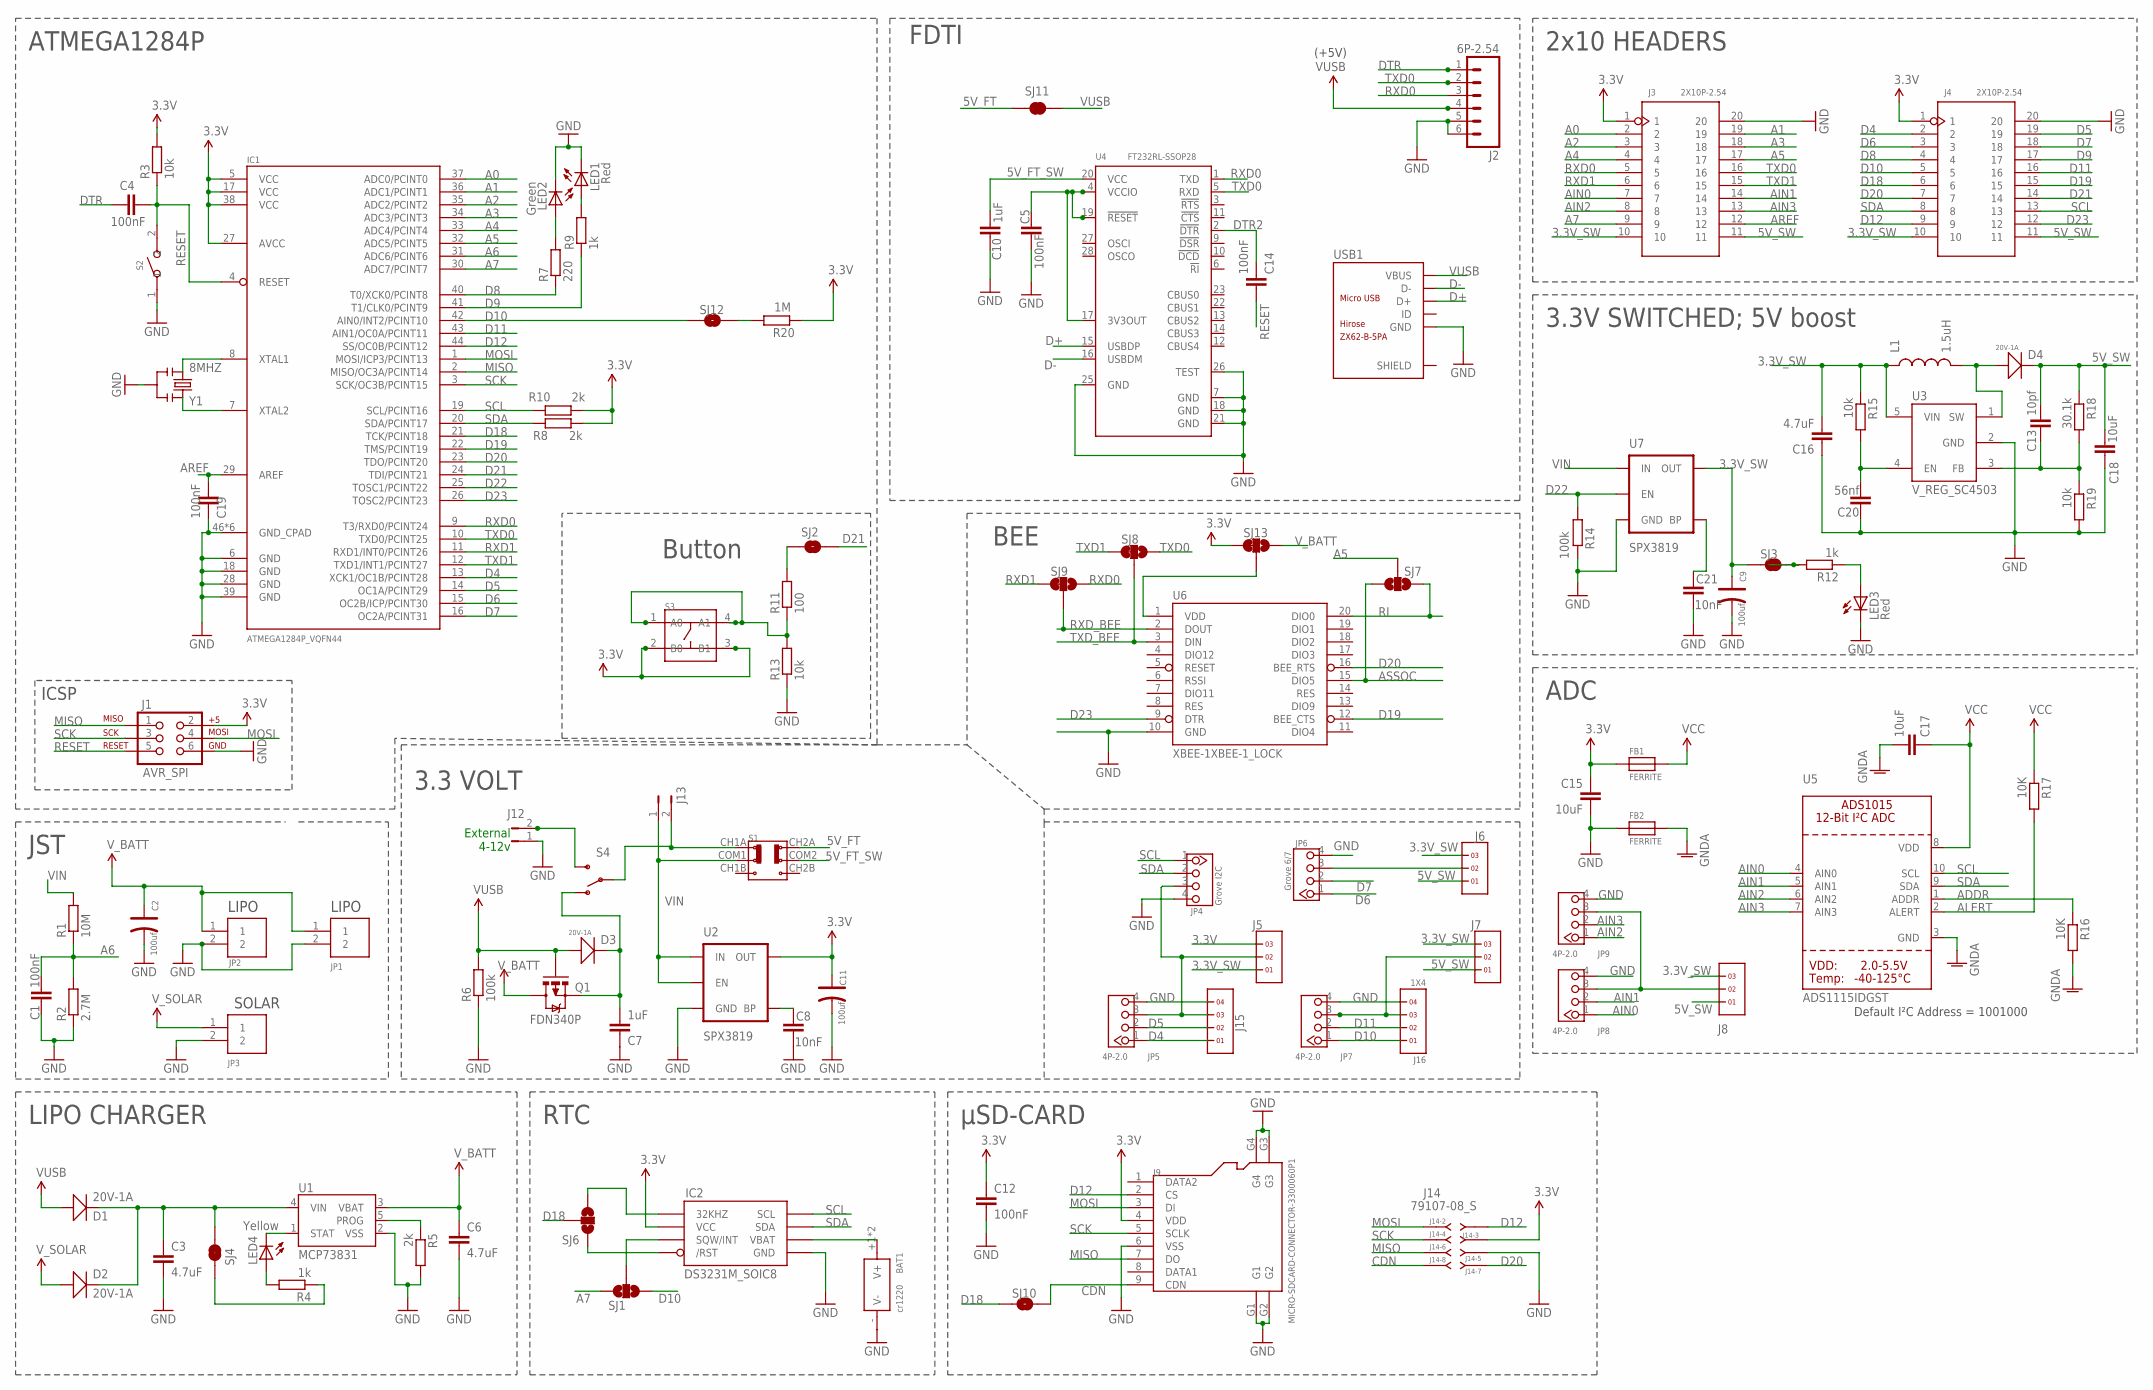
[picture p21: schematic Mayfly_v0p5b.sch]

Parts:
BAT1: cr1220; BAT2P-13.5-CR1220
C1, C4, C5, C12, C14, C19: 100nF; C0603
C2, C9, C11: 100uf; AVX-B
C3, C6: 4.7uF; C0603
C7, C10: 1uF; C0603
C8, C21: 10nF; C0603
C13: 10pf; 0603-CAP
C15, C17: 10uF; C0603
C16: 4.7uF; 0805
C18: 10uF; 0805
C20: 56nf; 0603-CAP
D1, D2, D3, D4: 20V-1A; SOD-123
FB1, FB2: FERRITE; 0805
IC1: ATMEGA1284P_VQFN44; VQFN44
IC2: DS3231M_SOIC8; SO8
J1: AVR_SPI; 2X3-NS
J2: 6P-2.54; 1X06_FEMALE_LOCK.010
J3, J4: 2X10P-2.54; H2X10-2.54
J5, J6, J7, J8: 1X3
J9: MICRO-SDCARD-CONNECTOR-3300060P1; 9P-SMD-W-RING
J12, J13: JUMPER-PTH-2-NO; PTH-JUMPER-2-NO_NO_SILK
J14: 79107-08_S; 79107-08
J15, J16: 1X4
JP1, JP2, JP3: JST_EPH_2PIN; JST_EPH_B2B-PH-K-S
JP4: Grove I2C; HW4-2.0
JP5, JP7, JP8, JP9: 4P-2.0; HW4-2.0
JP6: Grove 6/7; HW4-2.0
L1: 1.5uH; VLF4012A
LED1, LED3: Red; LED-0603
LED2: Green; LED-0603
LED4: Yellow; LED-0603
Q1: FDN340P; SOT23-S-PADS
R1: 10M; R0603
R2: 2.7M; R0603
R3, R13, R15, R19: 10k; R0603
R4, R9, R12: 1k; R0603
R5, R8, R10: 2k; R0603
R6, R14: 100k; R0603
R7: 220; R0603
R11: 100; R0603
R16, R17: 10K; R0603
R18: 30.1k; R0603
R20: 1M; R0603
S1: SWITCH-2CH-6P-3010010P1; 6P-2CH-2.54-9.1X3.5X3.2+2H
S2: SMD-BUTTON(2P-6.0X3.0X2.5MM)-DHT-1163S; SW2-4.0-6.0X3.0X2.5MM
S3: SMD-SWITCH-TACTILE-SPST-NO(4P-D6.0MM); SW4-SMD-6.0X6.0X5.0MM
S4: SWITCH-SPDT-SMD-A; SWITCH-SPST-SMD-A
SJ1, SJ6, SJ7: SOLDERJUMPER_2WAYT; SJ_2
SJ2, SJ3, SJ10, SJ12: SOLDERJUMPERNO; SJ_2S-NO
SJ4: SOLDERJUMPER_NC; SJ_2S_NC
SJ8, SJ9, SJ13: SJ_3WAY_12SHORT
SJ11: JUMPER-PAD-2-NC_BY_TRACENO_SILK; PAD-JUMPER-2-NC_BY_TRACE_NO_SILK
U1: MCP73831; SOT23-5
U2, U7: SPX3819; SOT23-5
U3: V_REG_SC4503; SOT23-5
U4: FT232RL-SSOP28; SSOP28-0.65-10.2X5.2MM
U5: ADS1115IDGST; MSOP10
U6: XBEE-1XBEE-1_LOCK; XBEE-1_LOCK
USB1: ZX62-B-5PA; MICRO-USB5+6P-SMD-0.65-AB
Y1: 8MHZ; X3-SMD-3.6X1.3X0.8MM

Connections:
1.8V: D2.+, JP3.1
3.3V: C11.+, C12.2, C15.1, FB1.1, IC1.5 (VCC), IC1.17 (VCC), IC1.27 (AVCC), IC1.38 (VCC), IC2.2 (VCC), J1.2, J3.1, J4.1, J5.3, J9.4 (VDD), J14.3, R3.2, R8.1, R10.2, R20.2, S3.2 (B0), S3.3 (B1), SJ13.1, U2.5 (OUT)
3.3V_SW: C9.+, C16.2, J3.10, J4.10, J5.1, J6.3, J7.3, J8.3, L1.P$1 (1), R15.1, SJ3.1, U3.5 (VIN), U7.5 (OUT)
5V_FT: S1.CH2A, SJ11.1
5V_FT_SW: C10.2, S1.COM2, U4.20 (VCC)
5V_SW: C13.2, C18.1, D4.-, J3.11, J4.11, J6.1, J7.1, J8.1, R18.1
A0: IC1.37 (ADC0/PCINT0), J3.2
A1: IC1.36 (ADC1/PCINT1), J3.19
A2: IC1.35 (ADC2/PCINT2), J3.3
A3: IC1.34 (ADC3/PCINT3), J3.18
A4: IC1.33 (ADC4/PCINT4), J3.4
A5: IC1.32 (ADC5/PCINT5), J3.17, SJ7.2
A6: C1.2, IC1.31 (ADC6/PCINT6), R1.1, R2.2
A7: IC1.30 (ADC7/PCINT7), J3.9, SJ1.3
ADDR: R16.1, U5.1 (ADDR)
AIN0: J3.7, JP8.1, U5.4 (AIN0)
AIN1: J3.14, JP8.2, U5.5 (AIN1)
AIN2: J3.8, JP9.1, U5.6 (AIN2)
AIN3: J3.13, JP9.2, U5.7 (AIN3)
ALERT: R17.2, U5.2 (ALERT)
AREF: C19.2, IC1.29 (AREF), J3.12
ASSOC: SJ7.3, U6.15 (DIO5)
C: IC1.8 (XTAL1), Y1.1
CDN: J9.9 (CDN), J14.8, SJ10.2
C_N: IC1.7 (XTAL2), Y1.3
D4: IC1.13 (XCK1/OC1B/PCINT28), J4.2, J15.1, JP5.1
D5: IC1.14 (OC1A/PCINT29), J4.19, J15.2, JP5.2
D6: IC1.15 (OC2B/ICP/PCINT30), J4.3, JP6.1
D7: IC1.16 (OC2A/PCINT31), J4.18, JP6.2
D8: IC1.40 (T0/XCK0/PCINT8), J4.4, R7.1
D9: IC1.41 (T1/CLK0/PCINT9), J4.17, R9.1
D10: IC1.42 (AIN0/INT2/PCINT10), J4.5, J16.1, JP7.1, SJ1.1, SJ12.1
D11: IC1.43 (AIN1/OC0A/PCINT11), J4.16, J16.2, JP7.2
D12: IC1.44 (SS/OC0B/PCINT12), J4.9, J9.2 (CS), J14.1
D18: IC1.21 (TCK/PCINT18), J4.6, SJ6.2, SJ10.1
D19: IC1.22 (TMS/PCINT19), J4.15, U6.12 (BEE_CTS)
D20: IC1.23 (TDO/PCINT20), J4.7, J14.7, U6.16 (BEE_RTS)
D21: IC1.24 (TDI/PCINT21), J4.14, SJ2.2
D22: IC1.25 (TOSC1/PCINT22), R14.2, U7.3 (EN)
D23: IC1.26 (TOSC2/PCINT23), J4.12, U6.9 (DTR)
D+: U4.15 (USBDP), USB1.3 (D+)
D-: U4.16 (USBDM), USB1.2 (D-)
DTR: C4.1, J2.1
DTR2: C14.2, U4.2 (!DTR)
GND: BAT1.- (V-), C1.1, C2.-, C3.2, C5.1, C6.2, C7.1, C8.1, C9.-, C10.1, C11.-, C12.1, C15.2, C16.1, C18.2, C19.1, C20.1, C21.1, FB2.1, IC1.6 (GND), IC1.18 (GND), IC1.28 (GND), IC1.39 (GND), IC1.46 (GND_CPAD), IC1.GND@0 (GND_CPAD), IC1.GND@1 (GND_CPAD), IC1.GND@2 (GND_CPAD), IC1.GND@3 (GND_CPAD), IC1.GND@4 (GND_CPAD), IC2.5 (GND), J1.6, J2.5, J2.6, J3.20, J4.20, J9.6 (VSS), J9.G1, J9.G2, J9.G3, J9.G4, J12.1, J14.5, J15.4, J16.4, JP1.2, JP2.2, JP3.2, JP4.4, JP5.4, JP6.4, JP7.4, JP8.4, JP9.4, LED1.C, LED2.C, LED3.C, R2.1, R5.2, R6.1, R13.1, R14.1, R19.2, S2.1, U1.2 (VSS), U2.2 (GND), U3.2 (GND), U4.7 (GND), U4.18 (GND), U4.21 (GND), U4.25 (GND), U4.26 (TEST), U6.10 (GND), U7.2 (GND), USB1.5 (GND), Y1.2
GNDA: C17.2, FB2.2, R16.2, U5.3 (GND)
LIPO_STAT: LED4.C, U1.1 (STAT)
MISO: IC1.2 (MISO/OC3A/PCINT14), J1.1, J9.7 (DO), J14.6
MOSI: IC1.1 (MOSI/ICP3/PCINT13), J1.4, J9.3 (DI), J14.2
unnamed: R20.1, SJ12.2
unnamed: C8.2, U2.4 (BP)
unnamed: R12.2, SJ3.2
unnamed: LED3.A, R12.1
unnamed: R11.1, R13.2, S3.1 (A0), S3.4 (A1)
unnamed: J8.2, JP8.3, JP9.3
unnamed: C5.2, U4.4 (VCCIO), U4.17 (3V3OUT), U4.19 (!RESET)
unnamed: D4.+, L1.P$2 (2), U3.1 (SW)
unnamed: SJ13.2, U6.1 (VDD)
unnamed: IC2.3 (SQW/INT), SJ1.2
unnamed: C7.2, D3.-, Q1.2 (S), S4.1 (O)
unnamed: LED4.A, R4.2
unnamed: R5.1, U1.5 (PROG)
unnamed: C3.1, D1.-, D2.-, SJ4.2, U1.4 (VIN)
unnamed: R4.1, SJ4.1
unnamed: J5.2, J15.3, JP4.3, JP5.3
unnamed: R11.2, SJ2.1
unnamed: J6.2, JP6.3
unnamed: J12.2, S4.3 (S)
unnamed: C21.2, U7.4 (BP)
unnamed: C13.1, R18.2, R19.1, U3.3 (FB)
unnamed: J7.2, J16.3, JP7.3
unnamed: J13.2, S1.CH1A, S4.2
unnamed: C20.2, R15.2, U3.4 (EN)
unnamed: LED1.A, R9.2
unnamed: BAT1.+1 (V+), BAT1.+2 (V+), IC2.6 (VBAT)
unnamed: LED2.A, R7.2
RESET: C4.2, C14.1, IC1.4 (RESET), J1.5, R3.1, S2.2
RI: SJ7.1, U6.20 (DIO0)
RTC_32KHZ: IC2.1 (32KHZ), SJ6.1
RTC_RST: IC2.4 (/RST), SJ6.3
RXD0: IC1.9 (T3/RXD0/PCINT24), J2.3, J3.5, SJ9.3, U4.1 (TXD)
RXD1: IC1.11 (RXD1/INT0/PCINT26), J3.6, SJ9.1
RXD_BEE: SJ9.2, U6.2 (DOUT)
SCK: IC1.3 (SCK/OC3B/PCINT15), J1.3, J9.5 (SCLK), J14.4
SCL: IC1.19 (SCL/PCINT16), IC2.8 (SCL), J4.13, JP4.1, R10.1, U5.10 (SCL)
SDA: IC1.20 (SDA/PCINT17), IC2.7 (SDA), J4.8, JP4.2, R8.2, U5.9 (SDA)
TXD0: IC1.10 (TXD0/PCINT25), J2.2, J3.16, SJ8.3, U4.5 (RXD)
TXD1: IC1.12 (TXD1/INT1/PCINT27), J3.15, SJ8.1
TXD_BEE: SJ8.2, U6.3 (DIN)
VCC: C17.1, FB1.2, R17.1, U5.8 (VDD)
VIN: J13.1, R1.2, S1.COM1, U2.1 (IN), U2.3 (EN), U7.1 (IN)
VUSB: D1.+, D3.+, J2.4, Q1.1 (G), R6.2, SJ11.2, USB1.1 (VBUS)
V_BATT: C2.+, C6.1, JP1.1, JP2.1, Q1.3 (D), SJ13.3, U1.3 (VBAT)

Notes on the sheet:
ATMEGA1284P
BEE
JST
RTC
SOLAR
LIPO
LIPO CHARGER
3.3 VOLT
(+5V)
FDTI
µSD-CARD
ICSP
ADC
Default I²C Address = 1001000
2x10 HEADERS
3.3V SWITCHED; 5V boost
Button
External 4-12v

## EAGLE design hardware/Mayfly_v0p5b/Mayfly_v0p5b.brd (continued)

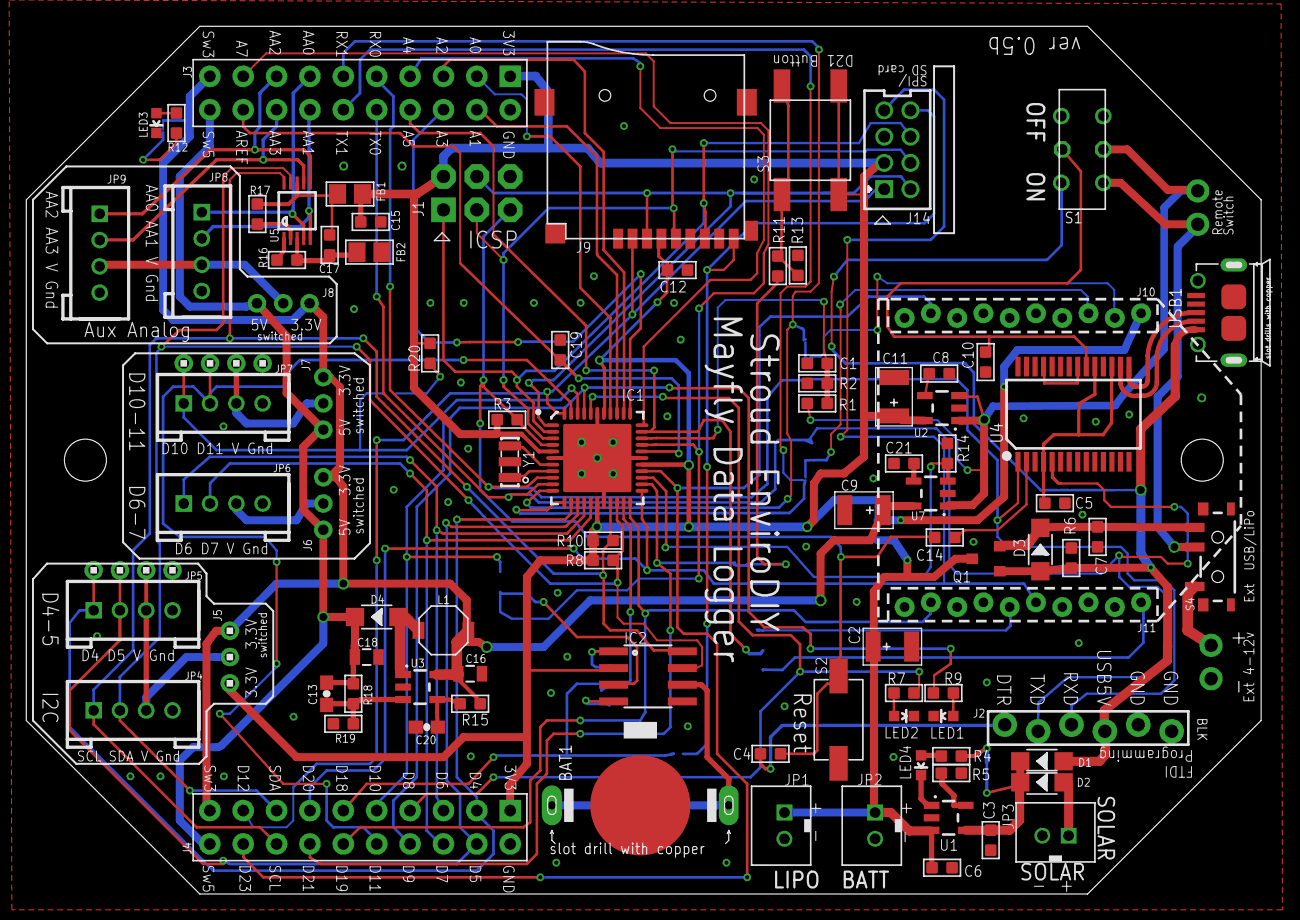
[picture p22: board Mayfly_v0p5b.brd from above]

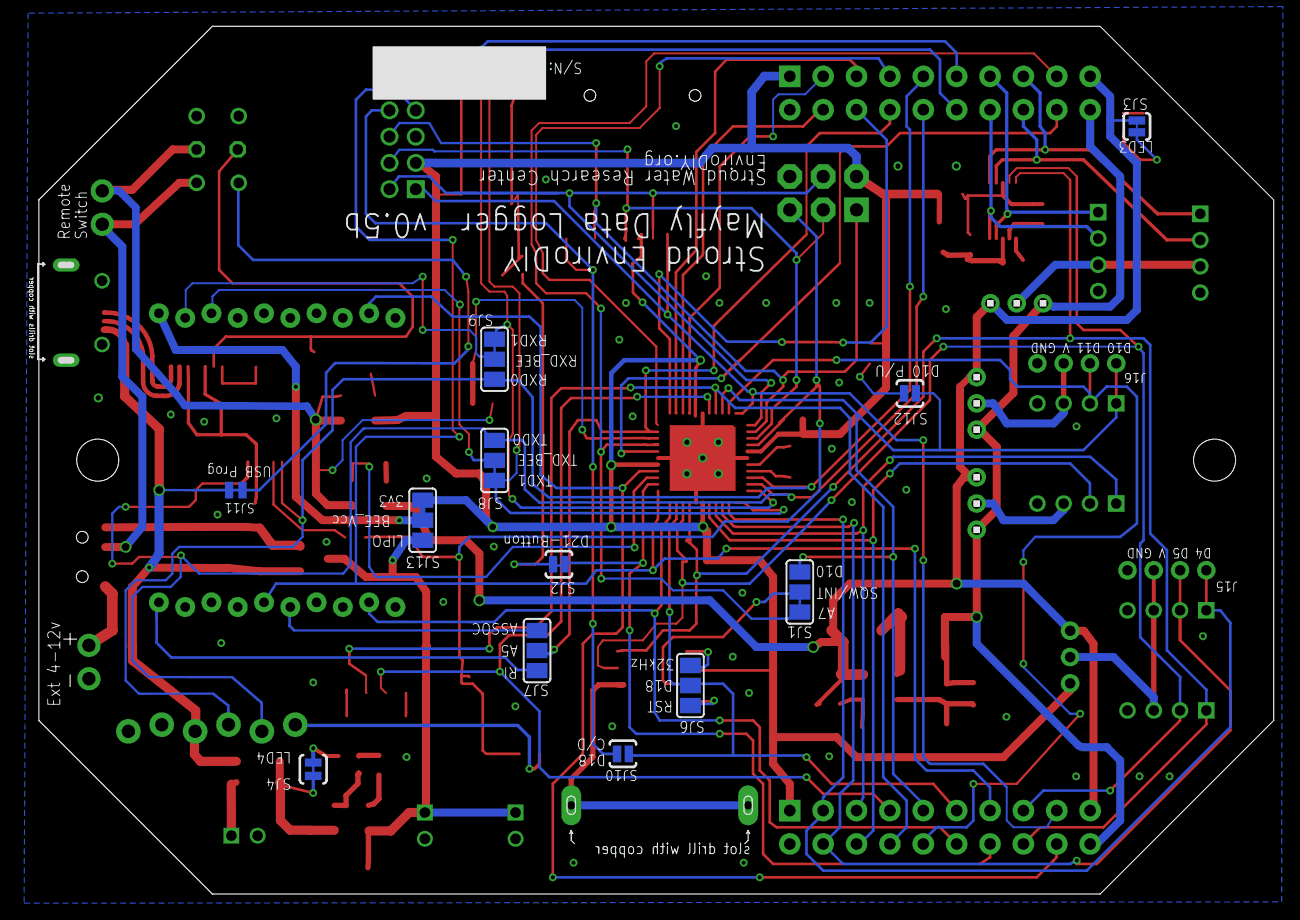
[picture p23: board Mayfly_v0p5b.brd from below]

Board: 4 copper layers, 94.0 x 66.0 mm, 104 parts (15 on the bottom side), 93 nets.

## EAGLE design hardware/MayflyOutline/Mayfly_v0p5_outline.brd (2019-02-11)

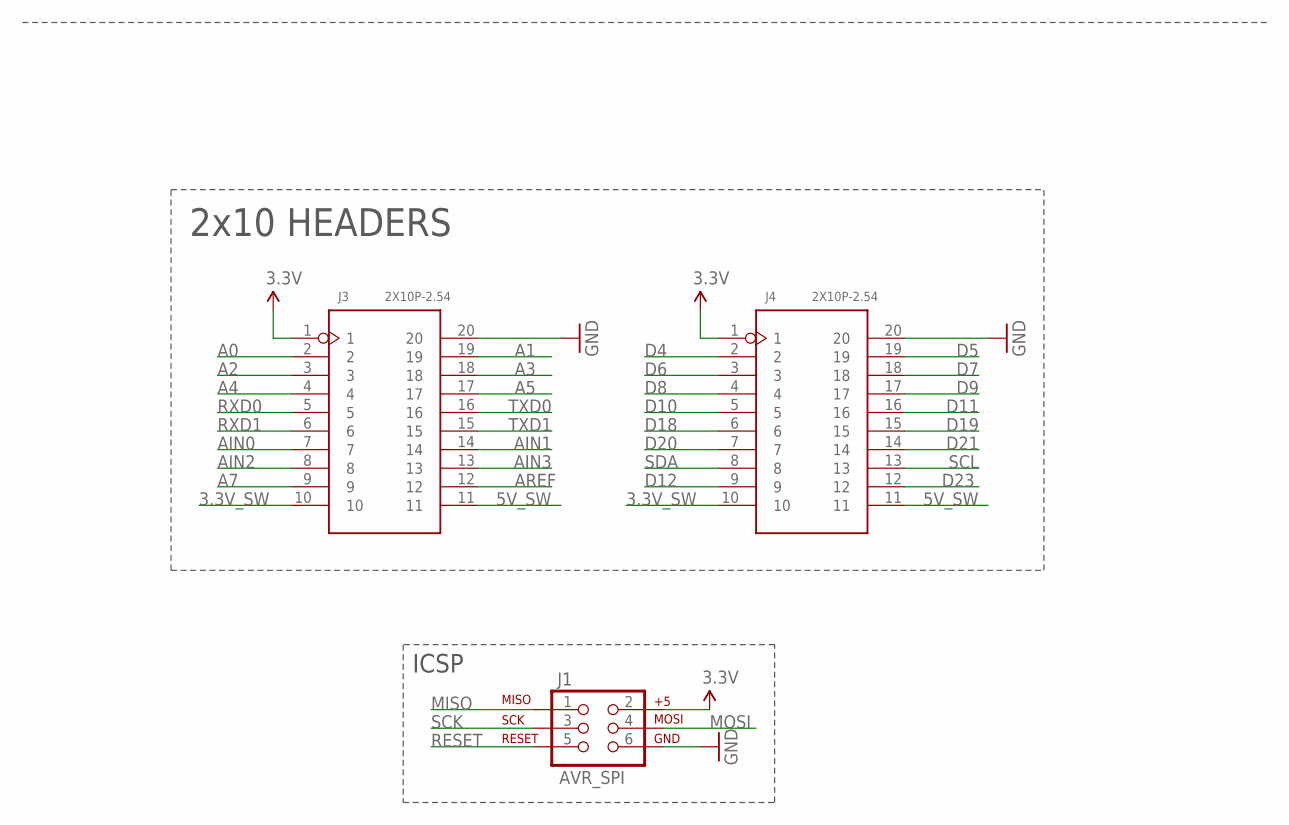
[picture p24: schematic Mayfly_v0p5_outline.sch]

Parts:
J1: AVR_SPI; 2X3-NS
J3, J4: 2X10P-2.54; H2X10-2.54

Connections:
3.3V: J1.2, J3.1, J4.1
3.3V_SW: J3.10, J4.10
5V_SW: J3.11, J4.11
A0: J3.2
A1: J3.19
A2: J3.3
A3: J3.18
A4: J3.4
A5: J3.17
A7: J3.9
AIN0: J3.7
AIN1: J3.14
AIN2: J3.8
AIN3: J3.13
AREF: J3.12
D4: J4.2
D5: J4.19
D6: J4.3
D7: J4.18
D8: J4.4
D9: J4.17
D10: J4.5
D11: J4.16
D12: J4.9
D18: J4.6
D19: J4.15
D20: J4.7
D21: J4.14
D23: J4.12
GND: J1.6, J3.20, J4.20
MISO: J1.1
MOSI: J1.4
RESET: J1.5
RXD0: J3.5
RXD1: J3.6
SCK: J1.3
SCL: J4.13
SDA: J4.8
TXD0: J3.16
TXD1: J3.15

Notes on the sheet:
ICSP
2x10 HEADERS

Board: 4 copper layers, 3 parts (0 on the bottom side), 4 nets, no tracks yet.

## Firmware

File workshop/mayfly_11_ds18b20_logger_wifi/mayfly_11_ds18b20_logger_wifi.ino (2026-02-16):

/** =========================================================================
 * @file DRWI_SIM7080LTE.ino
 * @brief Example for DRWI CitSci LTE sites.
 *
 * This example shows proper settings for the following configuration:
 *
 * Mayfly v1.x board
 * EnviroDIY ESP32 Wifi Module
 * Hydros21 CTD sensor
 *
 * @author Sara Geleskie Damiano <sdamiano@stroudcenter.org>
 * @copyright (c) 2017-2022 Stroud Water Research Center (SWRC)
 *                          and the EnviroDIY Development Team
 *            This example is published under the BSD-3 license.
 *

 * Hardware Platform: EnviroDIY Mayfly Arduino Datalogger
 *
 * DISCLAIMER:
 * THIS CODE IS PROVIDED "AS IS" - NO WARRANTY IS GIVEN.
 * ======================================================================= */

// ==========================================================================
//  Defines for the Arduino IDE
//  NOTE:  These are ONLY needed to compile with the Arduino IDE.
//         If you use PlatformIO, you should set these build flags in your
//         platformio.ini
// ==========================================================================
/** Start [defines] */
#ifndef TINY_GSM_RX_BUFFER
#define TINY_GSM_RX_BUFFER 64
#endif
#ifndef TINY_GSM_YIELD_MS
#define TINY_GSM_YIELD_MS 2
#endif
/** End [defines] */

// ==========================================================================
//  Include the libraries required for any data logger
// ==========================================================================
/** Start [includes] */
// The Arduino library is needed for every Arduino program.
#include <Arduino.h>

// EnableInterrupt is used by ModularSensors for external and pin change
// interrupts and must be explicitly included in the main program.
#include <EnableInterrupt.h>

// Include the main header for ModularSensors
#include <ModularSensors.h>
/** End [includes] */


// ==========================================================================
//  Data Logging Options
// ==========================================================================
/** Start [logging_options] */
// The name of this program file
const char* sketchName = "DRWI_SIM7080LTE.ino";
// Logger ID, also becomes the prefix for the name of the data file on SD card
const char* LoggerID = "DS18b20_wifi_example";      //replace the text between the quotation marks with your station's ID
// How frequently (in minutes) to log data
const uint8_t loggingInterval = 1;            
// Your logger's timezone.
const int8_t timeZone = -5;  // Eastern Standard Time
// NOTE:  Daylight savings time will not be applied!  Please use standard time!

// Set the input and output pins for the logger
// NOTE:  Use -1 for pins that do not apply
const int32_t serialBaud = 57600;  // Baud rate for debugging
const int8_t  greenLED   = 8;      // Pin for the green LED
const int8_t  redLED     = 9;      // Pin for the red LED
const int8_t  buttonPin  = 21;     // Pin for debugging mode (ie, button pin)
const int8_t  wakePin    = 31;     // MCU interrupt/alarm pin to wake from sleep
// Mayfly 0.x D31 = A7
const int8_t sdCardPwrPin   = -1;  // MCU SD card power pin
const int8_t sdCardSSPin    = 12;  // SD card chip select/slave select pin
const int8_t sensorPowerPin = 22;  // MCU pin controlling main sensor power
/** End [logging_options] */


// ==========================================================================
//  Wifi/Cellular Modem Options
// ==========================================================================
/** Start [espressif_esp32] */
#include <modems/EspressifESP32.h>

// Create a reference to the serial port for the modem
HardwareSerial& modemSerial = Serial1;  // Use hardware serial if possible
const int32_t   modemBaud   = 115200;   // Communication speed of the modem

// Modem Pins - Describe the physical pin connection of your modem to your board
// NOTE:  Use -1 for pins that do not apply
// Example pins here are for a EnviroDIY ESP32 Bluetooth/Wifi Bee with
// Mayfly 1.x
const int8_t modemVccPin    = 18;      // MCU pin controlling modem power
const int8_t modemResetPin  = -1;      // MCU pin connected to modem reset pin
const int8_t modemLEDPin    = redLED;  // MCU pin connected an LED to show modem
                                       // status

// Network connection information
// Enter the wifi network name and password below, making sure to enclose them in the quotation marks
const char* wifiId  = "xxxxxxxxxx";  // WiFi access point name
const char* wifiPwd = "xxxxxxxxxx";  // WiFi password (WPA2)


// Create the modem object
EspressifESP32 modemESP(&modemSerial, modemVccPin, modemResetPin, wifiId, wifiPwd);

// Create an extra reference to the modem by a generic name
EspressifESP32 modem = modemESP;
/** End [espressif_esp32] */



// ==========================================================================
//  Using the Processor as a Sensor
// ==========================================================================
/** Start [processor_sensor] */
#include <sensors/ProcessorStats.h>

// Create the main processor chip "sensor" - for general metadata
const char*    mcuBoardVersion = "v1.1";
ProcessorStats mcuBoard(mcuBoardVersion);
/** End [processor_sensor] */


// ==========================================================================
//  Maxim DS3231 RTC (Real Time Clock)
// ==========================================================================
/** Start [ds3231] */
#include <sensors/MaximDS3231.h>

// Create a DS3231 sensor object
MaximDS3231 ds3231(1);
/** End [ds3231] */


// ==========================================================================
//  Sensirion SHT4X Digital Humidity and Temperature Sensor
//  Built in on Mayfly 1.x
// ==========================================================================
/** Start [sensirion_sht4x] */
#include <sensors/SensirionSHT4x.h>

// NOTE: Use -1 for any pins that don't apply or aren't being used.
const int8_t SHT4xPower     = sensorPowerPin;  // Power pin
const bool   SHT4xUseHeater = true;

// Create an Sensirion SHT4X sensor object
SensirionSHT4x sht4x(SHT4xPower, SHT4xUseHeater);
/** End [sensirion_sht4x] */

// ==========================================================================
//  Maxim DS18 One Wire Temperature Sensor
// ==========================================================================
/** Start [ds18] */
#include <sensors/MaximDS18.h>

// OneWire Address [array of 8 hex characters]
// If only using a single sensor on the OneWire bus, you may omit the address
// DeviceAddress OneWireAddress1 = {0x28, 0xFF, 0xBD, 0xBA, 0x81, 0x16, 0x03,
// 0x0C};
const int8_t OneWirePower = sensorPowerPin;  // Power pin (-1 if unconnected)
const int8_t OneWireBus   = 5;  // OneWire Bus Pin (-1 if unconnected)

// Create a Maxim DS18 sensor objects (use this form for a known address)
// MaximDS18 ds18(OneWireAddress1, OneWirePower, OneWireBus);

// Create a Maxim DS18 sensor object (use this form for a single sensor on bus
// with an unknown address)
MaximDS18 ds18(OneWirePower, OneWireBus);
/** End [ds18] */




// ==========================================================================
//  Creating the Variable Array[s] and Filling with Variable Objects
// ==========================================================================
/** Start [variable_arrays] */
Variable* variableList[] = {
    new MaximDS18_Temp(&ds18),  
    new SensirionSHT4x_Humidity(&sht4x),         // Relative humidity (Sensirion_SHT40_Humidity)       
    new ProcessorStats_Battery(&mcuBoard),
};

// All UUID's, device registration, and sampling feature information can be
// pasted directly from Monitor My Watershed.
// To get the list, click the "View  token UUID list" button on the upper right
// of the site page.

// *** CAUTION --- CAUTION --- CAUTION --- CAUTION --- CAUTION ***
// Check the order of your variables in the variable list!!!
// Be VERY certain that they match the order of your UUID's!
// Rearrange the variables in the variable list ABOVE if necessary to match!
// Do not change the order of the variables in the section below.
// *** CAUTION --- CAUTION --- CAUTION --- CAUTION --- CAUTION ***

// Replace all of the text in the following section with the UUID array from
// MonitorMyWatershed

/* clang-format off */
// ---------------------   Beginning of Token UUID List   ---------------------

const char *UUIDs[] =                                                      // UUID array for device sensors
{
    "233cd50f-2855-421f-ad4c-a5fec5cf73ca",   // Temperature (Maxim_DS18B20_Temp)
    "fc774e25-9669-4d46-b981-052a72adc8de",   // Relative humidity (Sensirion_SHT40_Humidity)
    "8d9d6c22-a8e5-4a43-b2e6-4bf657b8f0c9"    // Battery voltage (EnviroDIY_Mayfly_Batt)
};
const char *registrationToken = "b4391537-b1fd-4f7e-a532-77778bf2a485";   // Device registration token
const char *samplingFeature = "91f153d7-634f-4288-852e-a2279040dabf";     // Sampling feature UUID


// -----------------------   End of Token UUID List  -----------------------
/* clang-format on */

// Count up the number of pointers in the array
int variableCount = sizeof(variableList) / sizeof(variableList[0]);

// Create the VariableArray object
VariableArray varArray(variableCount, variableList, UUIDs);
/** End [variable_arrays] */


// ==========================================================================
//  The Logger Object[s]
// ==========================================================================
/** Start [loggers] */
// Create a new logger instance
Logger dataLogger(LoggerID, loggingInterval, &varArray);
/** End [loggers] */


// ==========================================================================
//  Creating Data Publisher[s]
// ==========================================================================
/** Start [publishers] */
// Create a data publisher for the Monitor My Watershed/EnviroDIY POST endpoint
#include <publishers/EnviroDIYPublisher.h>
EnviroDIYPublisher EnviroDIYPOST(dataLogger, &modem.gsmClient,
                                 registrationToken, samplingFeature);
/** End [publishers] */


// ==========================================================================
//  Working Functions
// ==========================================================================
/** Start [working_functions] */
// Flashes the LED's on the primary board
void greenredflash(uint8_t numFlash = 4, uint8_t rate = 75) {
    for (uint8_t i = 0; i < numFlash; i++) {
        digitalWrite(greenLED, HIGH);
        digitalWrite(redLED, LOW);
        delay(rate);
        digitalWrite(greenLED, LOW);
        digitalWrite(redLED, HIGH);
        delay(rate);
    }
    digitalWrite(redLED, LOW);
}

// Reads the battery voltage
// NOTE: This will actually return the battery level from the previous update!
float getBatteryVoltage() {
    if (mcuBoard.sensorValues[0] == -9999) mcuBoard.update();
    return mcuBoard.sensorValues[0];
}
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

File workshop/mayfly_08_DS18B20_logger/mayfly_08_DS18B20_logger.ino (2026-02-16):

//Sample sketch for logging DS18B20 temperature data to microSD card on EnviroDIY Mayfly 

#include <Wire.h>
#include "Sodaq_DS3231.h"
#include <SPI.h>
#include <SD.h>
#include <OneWire.h>
#include <DallasTemperature.h>

#define ONE_WIRE_BUS 5
//#define TEMPERATURE_PRECISION 11 

OneWire oneWire(ONE_WIRE_BUS);
DallasTemperature sensors(&oneWire);

#define SD_SS_PIN 12

#define FILE_NAME "Datafile.txt"
//Data header
#define LOGGERNAME "Mayfly DS18B20 Temperature Logger"  
#define DATA_HEADER "DateTime_UTC,Loggertime,BoardTempC,BatteryV,Sensor_Temp_C"

String dataRec = "";
int currentminute;
long currentepochtime = 0;
float boardtemp = 0.0;

int batteryPin = A6;    // select the input pin for the potentiometer
int batterysenseValue = 0;  // variable to store the value coming from the sensor
float batteryvoltage;       // the calculated battery voltage in volts

void setup () 
{
    Serial.begin(57600);
    Serial.println("Mayfly Workshop Multi-Sensor & microSD Logger");
    pinMode(8, OUTPUT);
    pinMode(9, OUTPUT);
    greenred4flash();   //blink the LEDs to show the board is on    
    digitalWrite(8, HIGH);
    Wire.begin();
    rtc.begin();
    setupLogFile();         
    sensors.begin();
//    sensors.setResolution(tempDeviceAddress, TEMPERATURE_PRECISION);
}

void loop () 
{ 
     dataRec = createDataRecord();
     sensormeasurements();
     logData(dataRec);
     Serial.print("Data Record: ");
     Serial.println(dataRec);      
     String dataRec = ""; 
  
     delay(5000);
}

void setupLogFile()
{
  //Initialise the SD card
  if (!SD.begin(SD_SS_PIN))
  {
    Serial.println("Error: SD card failed to initialise or is missing.");

    for (int r=1; r <= 10; r++)
    {
      digitalWrite(9, HIGH);
      delay(400);
      digitalWrite(9, LOW);
      delay(200);
    }
  
  }
  
  //Check if the file already exists
  bool oldFile = SD.exists(FILE_NAME);  
  
  //Open the file in write mode
  File logFile = SD.open(FILE_NAME, FILE_WRITE);
  
  //Add header information if the file did not already exist
  if (!oldFile)
  {
    logFile.println(LOGGERNAME);
    logFile.println(DATA_HEADER);
  }
  
  //Close the file to save it
  logFile.close();  
}


void logData(String rec)
{
  //Re-open the file
  File logFile = SD.open(FILE_NAME, FILE_WRITE);
  
  //Write the CSV data
  logFile.println(rec);
  
  //Close the file to save it
  logFile.close();  
}

String createDataRecord()
{
    //Create a String type data record in csv format
    String data = getDateTime();
    data += ",";
     
    rtc.convertTemperature();          //convert current temperature into registers
    boardtemp = rtc.getTemperature(); //Read temperature sensor value
    
    batterysenseValue = analogRead(batteryPin);
    batteryvoltage = (3.3/1023.) * 4.7 * batterysenseValue;
    
    data += currentepochtime;
    data += ",";

    addFloatToString(data, boardtemp, 3, 1);    //float   
    data += ",";  
    addFloatToString(data, batteryvoltage, 4, 2);
  
//  Serial.print("Data Record: ");
//  Serial.println(data);
  return data;
}


static void addFloatToString(String & str, float val, char width, unsigned char precision)
{
  char buffer[10];
  dtostrf(val, width, precision, buffer);
  str += buffer;
}

void sensormeasurements()
{
      sensors.requestTemperatures(); // Send the command to get temperatures
      float tempC = sensors.getTempCByIndex(0);

      dataRec += ",";
      addFloatToString(dataRec, tempC, 5, 3);
}

String getDateTime()
{
  String dateTimeStr;
  
  //Create a DateTime object from the current time
  DateTime dt(rtc.makeDateTime(rtc.now().getEpoch()));

  currentepochtime = (dt.get());    //Unix time in seconds 

  currentminute = (dt.minute());
  //Convert it to a String
  dt.addToString(dateTimeStr); 
  return dateTimeStr;  
}

uint32_t getNow()
{
  currentepochtime = rtc.now().getEpoch();
  return currentepochtime;
}
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

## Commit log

2016-07-22 Added sonar sensor examples
2017-01-08 Edits to Examples directory
    * added initial_demo_blink_temperature sketch, from
    http://envirodiy.org/mayfly/software/, so that people could reproduce
    if they overwrite it.
    * Updated ReadMe to reflect above
    * removed “_1” from “blinking_LEDs” sketch name, to match EnviroDIY
    website.
2017-02-02 changed serial baud rate, prints sketch name
2017-02-02 Made more generic, added exceptions, fixed exe
    Made the python in ino scripts more generic so they reference any FTDI
    device instead of the Mayfly. Also added more places to catch
    exceptions in the python script. Hopefully this will prevent the exe
    from just flashing open and closing again for people.
2017-02-03 Added #include <Arduino.h> statments for pio
2017-02-03 Now: #include <wire.h>. Sorry PIO!
2017-02-03 Wire, not wire.
2017-02-06 Updated Workshop 6 DHT docs
    To update documentation on the Adafruit library and to include docs on
    the Grove port power pin (22).
    Also mayfly_08_magnetswitch.ino
    Need to update all other Grove sketches with these comments.
2017-02-07 Got simple_logging_example working
    Got the simple_logging_example working using Shannon's timer functions.
    Also fixed the usu script to not always print success. Removed the
    broken "logging_to_pc" script. Also removed the sync_clock_pc because
    that is now an example in the Sodaq library.
2017-02-13 Update documentation on Example:Battery
    examples/battery_measurement.ino
2017-02-19 Added dreamhost to modular sensor sending
2017-02-20 modular sensors are working!
2017-03-01 Initial commit of mayfly_11_DT-LED branch
    LimnoTech team is trying to mod 10-sonar by replacing Maxbotix sonar
    with Waterproof DS18B20 Digital temperature sensor
2017-03-01 Works with Grove DHT 11 sensor
    We don’t have the resistor for the DS18B20 sensor (bummer)!
2017-03-08 Renamed files; created 10c for DS18B20 temperature
    Now have workshop sketches: 10 (Maxbotix), 10b (DHT), 10c (DS18B20
    Digital temperature)
2017-06-07 corrected readout to include temperature
2017-06-08 Sketch for Luminosity to display on LED
2017-06-22 Fixed DHT_LED
    Was printing humidity twice.
2018-01-08 Added schematics for 3 main versions of boards
2018-01-09 Add files via upload
    Drilling guide for Pelican 1120 case. Contains measurements for cord grips, solar radiation shield, and sonar to attach directly to box. More info coming soon on blog.
2018-01-09 Updated luminosity sketch to use library with unified sensor driver
    Adafruit considers the other library (v1) to be obsolete
2019-02-12 Added arduino_boards submodule
2019-06-05 Exported Bill of Materials from Eagle
    I need to replace several fried RTCs and I am searching for the right part.
    DigiKey 8-footed DS3231 are DS3231MZ/V+-ND and DS3231MZ+-ND
    and it seems like either would work. @s-hicks2 or @bschulz1701, is the "/V" in the part number meaningful to you? Which one should I pick? My gut is the one not labeled as automotive.
    BOM says
    IC2 DS3231M_SOIC8 DS3231M_SOIC8 SO8
2019-12-11 Added links to Pelican drill template
    In ReadMe.md for Hardware.
2020-04-01 Add detail to battery voltage ReadMe
2020-04-01 Fix backward voltage level in text
2020-04-01 Correct LED colors
2020-04-21 Update battery_measurement.ino
    Corrected voltage divider ratio
2020-04-21 Update ReadMe.md
    corrected voltage divider ratio

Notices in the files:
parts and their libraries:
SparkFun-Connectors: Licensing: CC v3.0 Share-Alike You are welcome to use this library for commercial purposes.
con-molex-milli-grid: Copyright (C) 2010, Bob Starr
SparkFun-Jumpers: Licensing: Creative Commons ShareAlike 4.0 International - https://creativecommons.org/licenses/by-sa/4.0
